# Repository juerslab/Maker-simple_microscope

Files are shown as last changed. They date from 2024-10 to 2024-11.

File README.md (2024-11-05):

# Name: simple_microscope
This microscope grew out of a need created by the pandemic, during Spring 2020. To implement a brownian motion lab for a biophysics lab course, I built microscopes similar to this, and the students carried out the experiment at their homes.

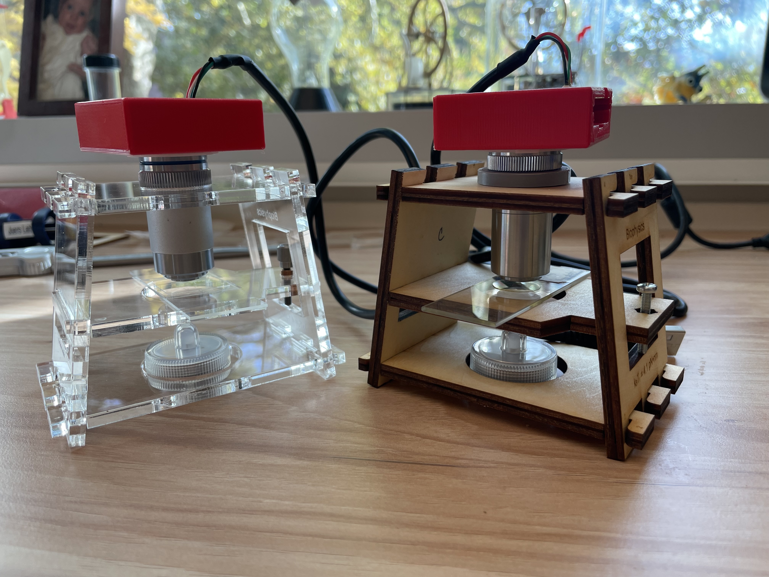
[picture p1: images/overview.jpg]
  

The microscope on the left uses acrylic and a fine adjuster. The microscope on the right uses plywood, a coarse adjuster, and the objective spacer (required for the second Amscope objective - see below)  

Microscope with image of 1 micron polystyrene beads imaged with the microscope:  

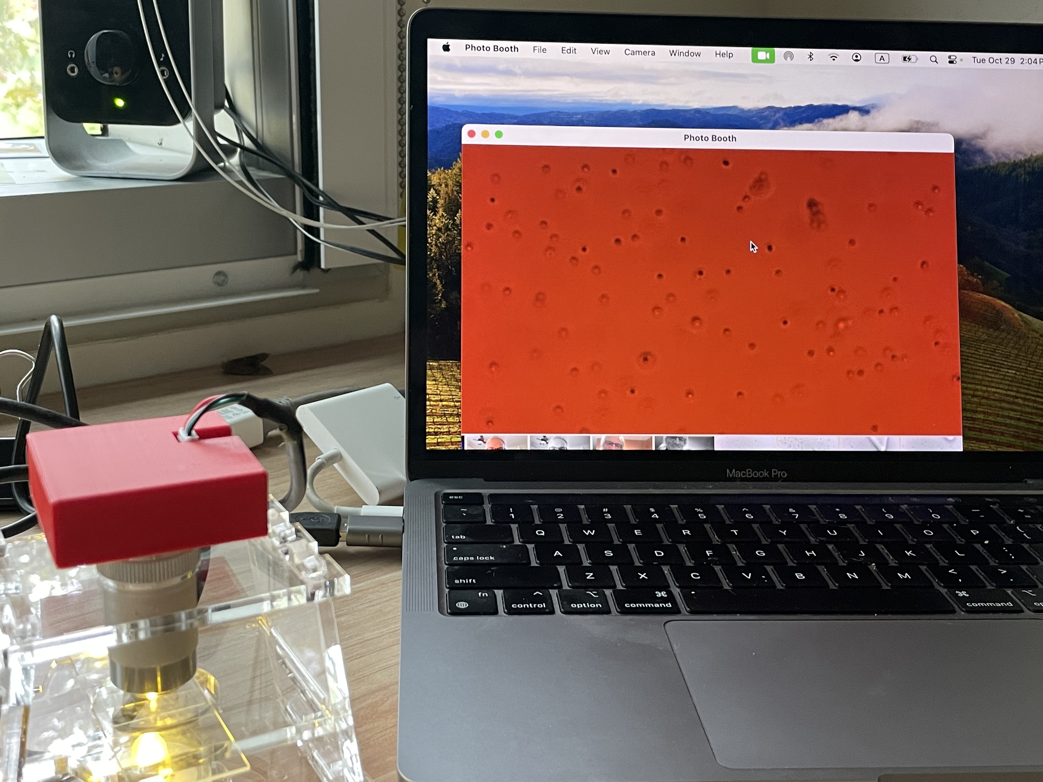
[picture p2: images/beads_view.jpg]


## Description & Parts
The microscope includes the following parts:

### Objective lens
The microscope is designed for an objective with RMS threading and a parfocal length of about 45 mm. We use these ~$25 objectives from Amscope:  
- https://amscope.com/products/a40x-v300?variant=40347660681391 
or:
- https://amscope.com/products/a40x-yx-v460 (This objective requires the use of a spacer; see below.)

### Camera

Arducam camera chip: (here ~$30)
https://www.amazon.com/dp/B07YHK63DS?ref=ppx_yo2ov_dt_b_fed_asin_title&th=1

### Light source

A small tea light works:
https://www.amazon.com/dp/B07654MKZH?ref=ppx_yo2ov_dt_b_fed_asin_title&th=1

### Camera housing

3D printed with an FDM printer. Also requires a 3D printed adapter for attaching the objective. 

### Framework

Laser cut from nominal 3/16" thick acrylic or plywood. 

### Vertical translation 

There are two options:
- Coarse:  Using a 20 mm M3x0.5 bolt with M3x0.5 mm nut
- Fine: Using a 25 mm M3x0.20 adjuster from Thorlabs
    - F3ES25
    - F3ESK1
    - F3ESN1P
    
### Misc parts (both 3D printed)

- Spacer ring if the second Amscope objective above is used
- Tool to help remove lens

## Creating the necessary parts. All parts were designed in OpenSCAD (see objects folder).
### 3D Printed parts
We print these with an FDM printer (Raise3D Pro 3 with hyperspeed option), using standard parameters. They are designed to be printed without supports, with the z-axis in OpenSCAD pointing up on the printer (this is the default orientation when the stl files are imported into IdeaMaker for the Raise3D printer.)
1. Camera housing
    - v3 is for the current model of the camera (11/24)
    - v1.1 is for an older model of the camera
2. Objective-camera housing adapter
3. Objective spacer (if using the second Amscope objective)
4. Camera lens remover (tool to help remove the lens from the camera)

### Laser cut parts - microscope framework
We cut these using an Epilog Zing laser cutter/engraver, using nominal 3/16" thick acrylic or plywood.The actual thickness of products we have used seems to vary enough that one needs to measure the thickness of each piece before cutting.  
1. Measure thickness of stock using caliper, in mm. 
2. Adjust parameters in OpenSCAD code.
3. Export to DXF
4. Import DXF file into CorelDraw or Inkscape. If using labels, there is a default coreldraw file called simple_microscope_labels_only.cdr which can be used as a template. The dxf file can be imported on top of the labels, and its position adjusted.
5. Cut/engrave.  For our 60W Epilog Zing, the following Speed/Power values were used for nominal 3/16" thick material:

Table to get main OpenSCAD parameters.

| Material | Design         | Main Slot Height | Sample Platform Slot Height |
|----------|----------------|------------------|-----------------------------|
| Acrylic  | Slot           | d + 0.36 mm      | d + 0.37 mm  (?)            |
| Acrylic  | Interlocking   | d + 0.42 mm      | d + 0.37 mm                 |
| Plywood  | Slot           | d + 0.27 mm      | d + 0.42 mm                 |
| Plywood  | Interlocking   | d + 0.47 mm      | d + 0.42 mm                 |

- The above parameters can be considered to be a starting point.
- Note that the above acrylic parameters assume a smooth edge. If the edge is somewhat rough, then add about 0.1 mm. In our experience cast acrylic tends to produce rougher edges, and needs to have a larger slot width.
- If the slots are too wide, the whole framework can be shimmed. (See below.)
- If the slots are too small, the framework will get "frozen" after locking and break when taking apart; plywood is more forgiving.
- Other parameters that may need adjusting include hex_nut_radius and fine_thread_cylinder_radius, depending on hex nut size and laser kerf
 
Table to get laser power (for Epilog Zing, 60 W)
| Material (3/16) | Raster  |  Vector  |
|-----------------|---------|----------|
| Acrylic         | S90/P25 | S35/P100 |
| Plywood         | S90/P30 | S70/P65  |

## Assembly

Two views of the microscope:  

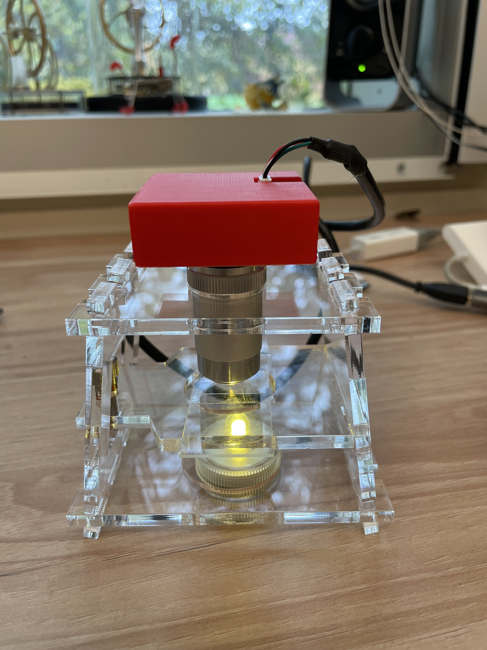
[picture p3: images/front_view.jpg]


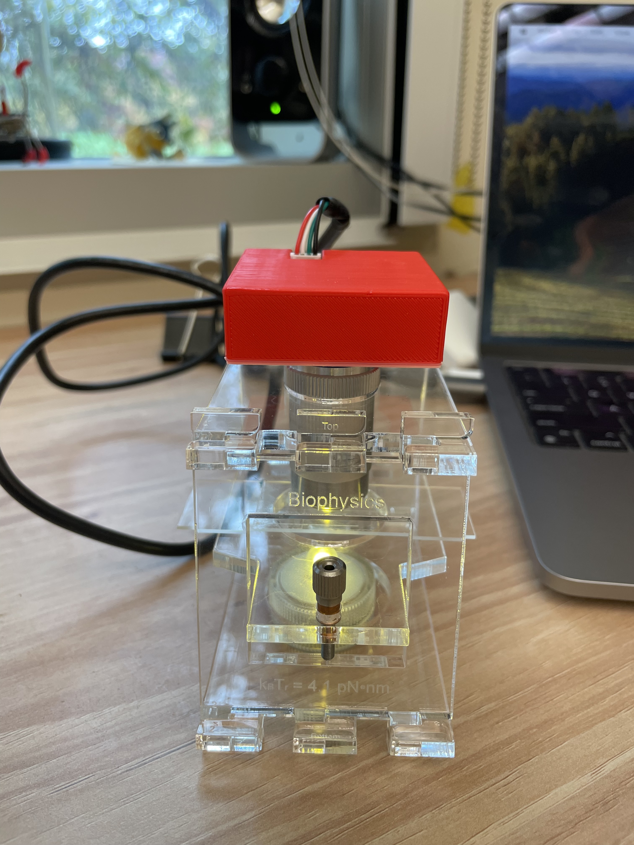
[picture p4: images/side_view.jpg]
  

### Step-by-step 
The parts of the microscope.  

  

1. The pieces interlock. Numbers indicate which pieces should be together. Attach the first side to the bottom and lock so that the 1s line up.   

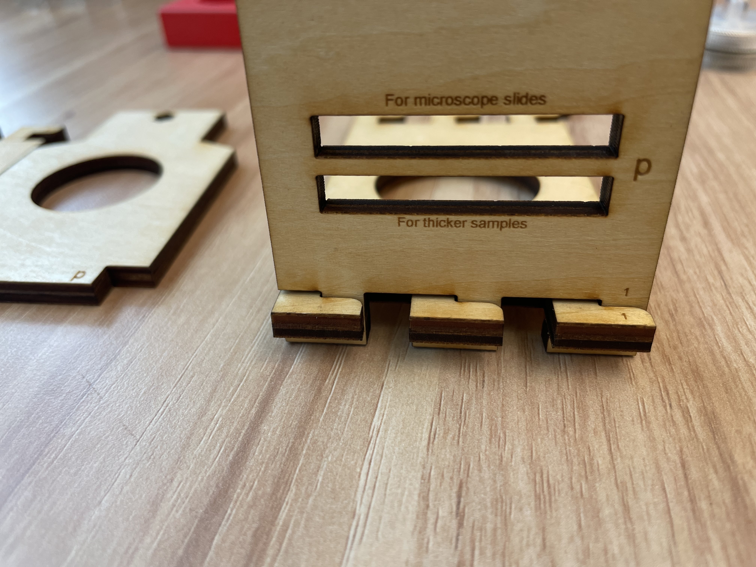
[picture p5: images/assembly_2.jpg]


2. Attach the other side.  
 
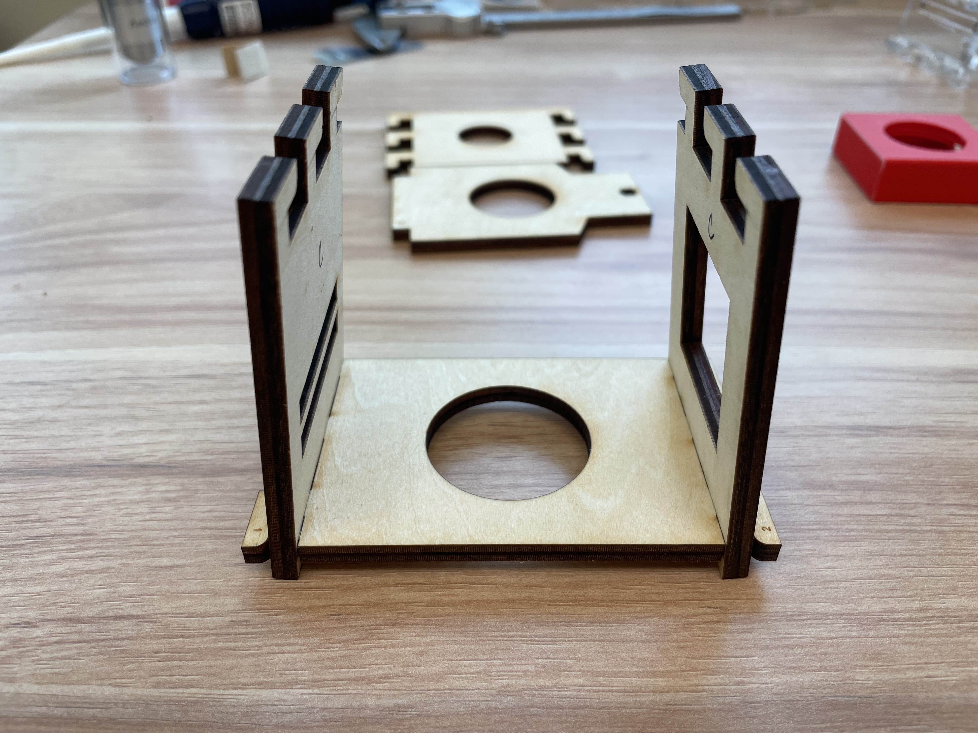
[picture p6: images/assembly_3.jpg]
  

3. Place the top onto both sides without locking.

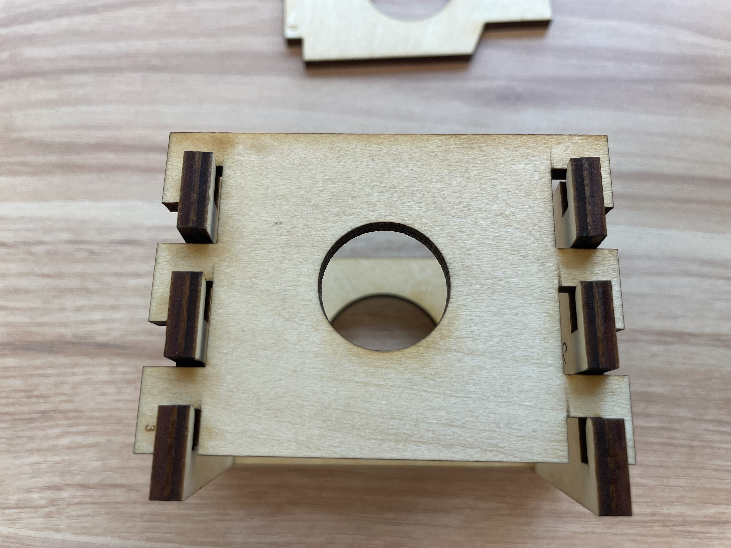
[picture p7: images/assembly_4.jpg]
  

4. Once the top is on both sides, then lock both sides simultaneously.

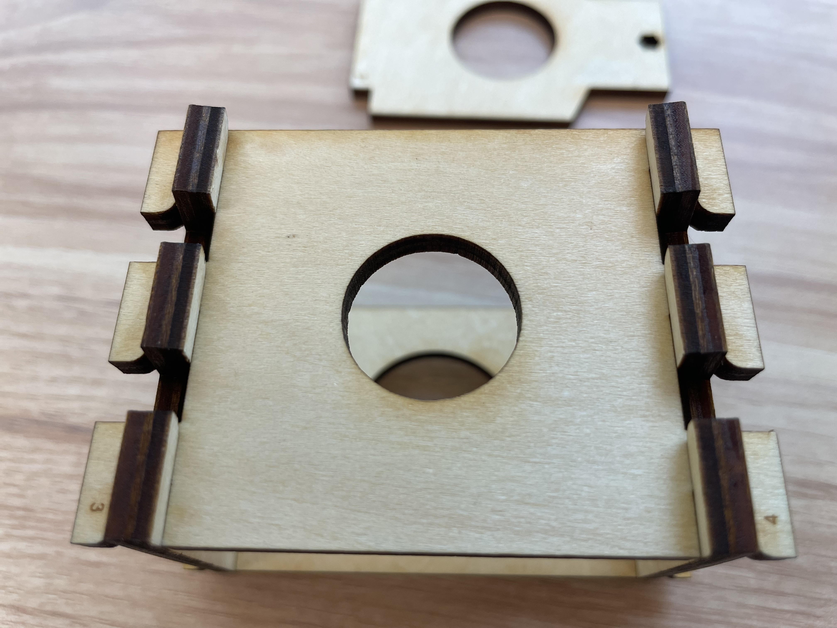
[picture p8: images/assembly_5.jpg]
 
   
5. The nut presses into a matching hold on the sample platform piece.

  

6. After pressing the nut in. If you use the fine adjustement, instead of a nut, you'll use a cylindrical sleeve.

  

7. Next slide the platform in so the tab with the nut enters the square hole on the side.

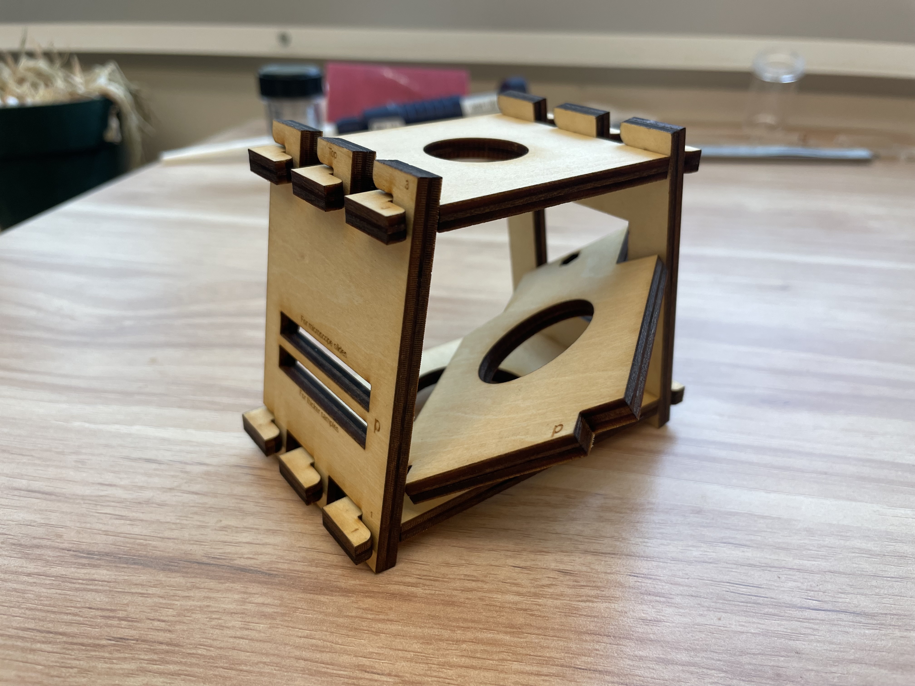
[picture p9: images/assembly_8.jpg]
  

8. Then place the other tab in the slot on the other side of the framework.

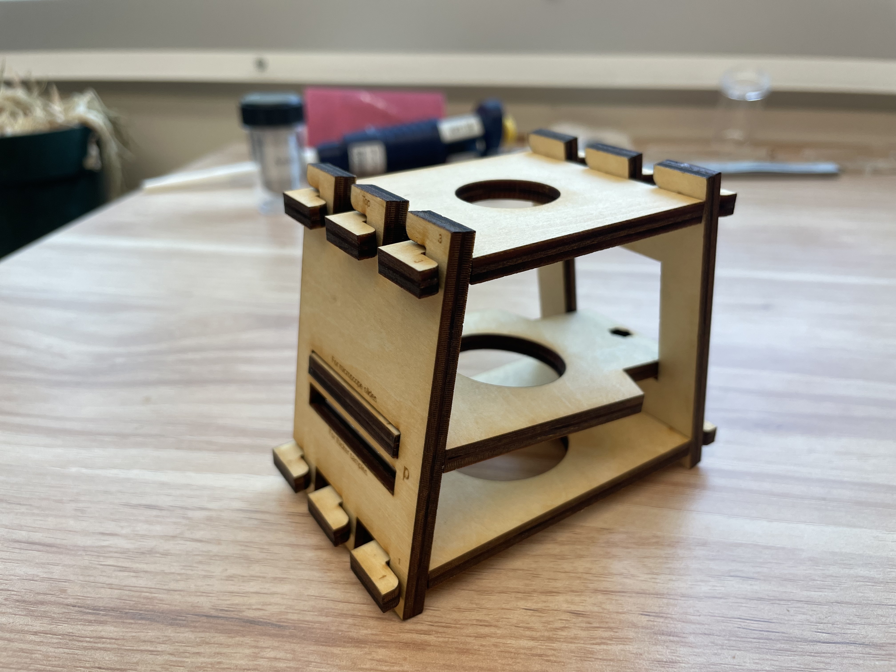
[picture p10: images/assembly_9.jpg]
  

9. Thread the bolt in the nut, and screw it in until the platform is level. The framework is finished. 

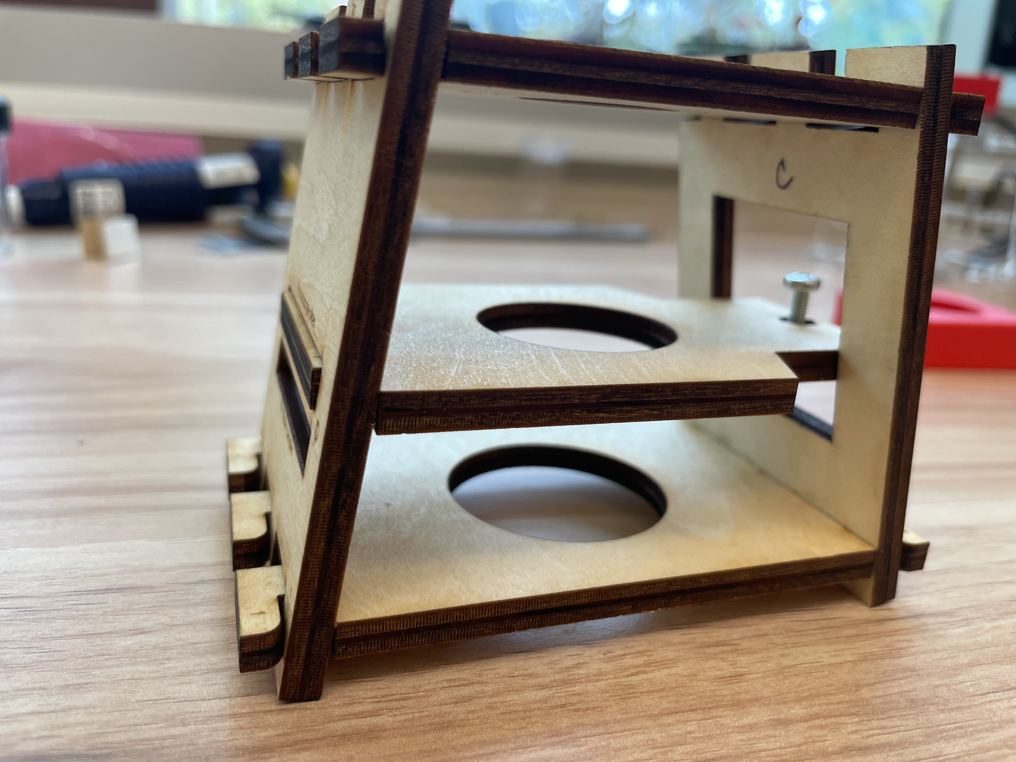
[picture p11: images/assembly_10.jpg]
  

10. The objective and objective_camera-housing adapter.

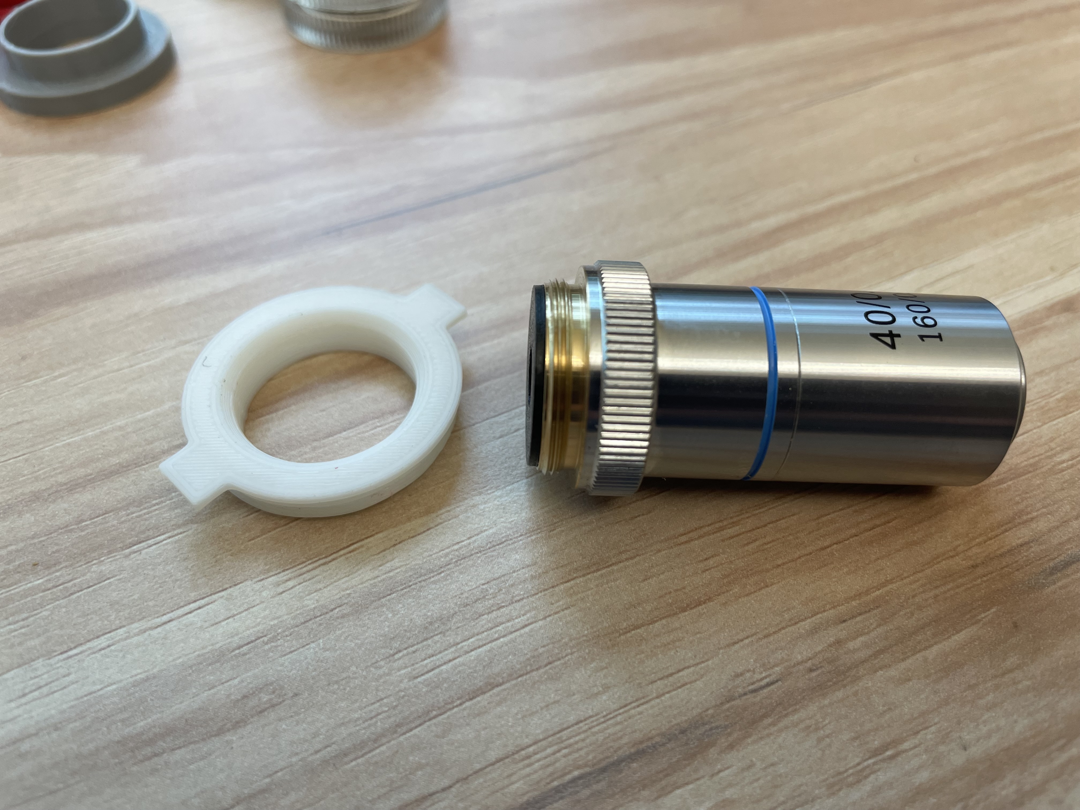
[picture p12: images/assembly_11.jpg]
  

11. Screw the adaptor onto the objective. Some fiddling may be required to get the threads correct. 
 
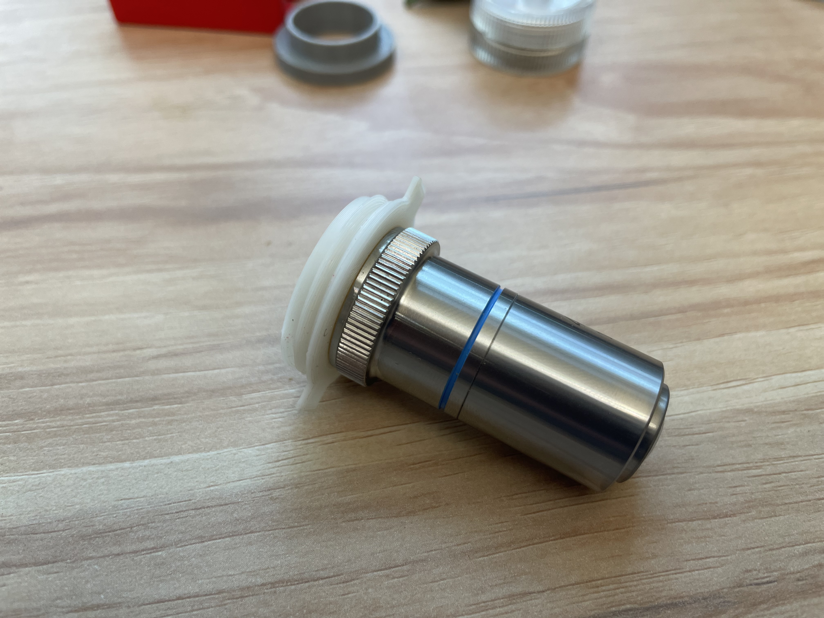
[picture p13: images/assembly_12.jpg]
  

12. Objective & adaptor with camera housing. Screw the adaptor into the camera housing.

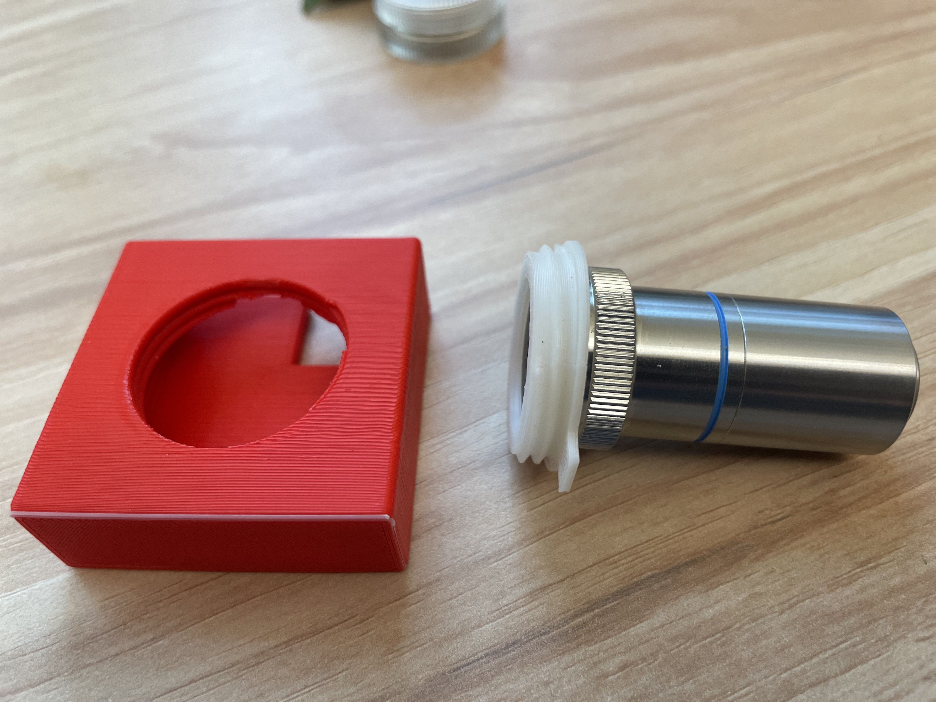
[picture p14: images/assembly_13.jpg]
  

13. Complete, waiting for the camera board.

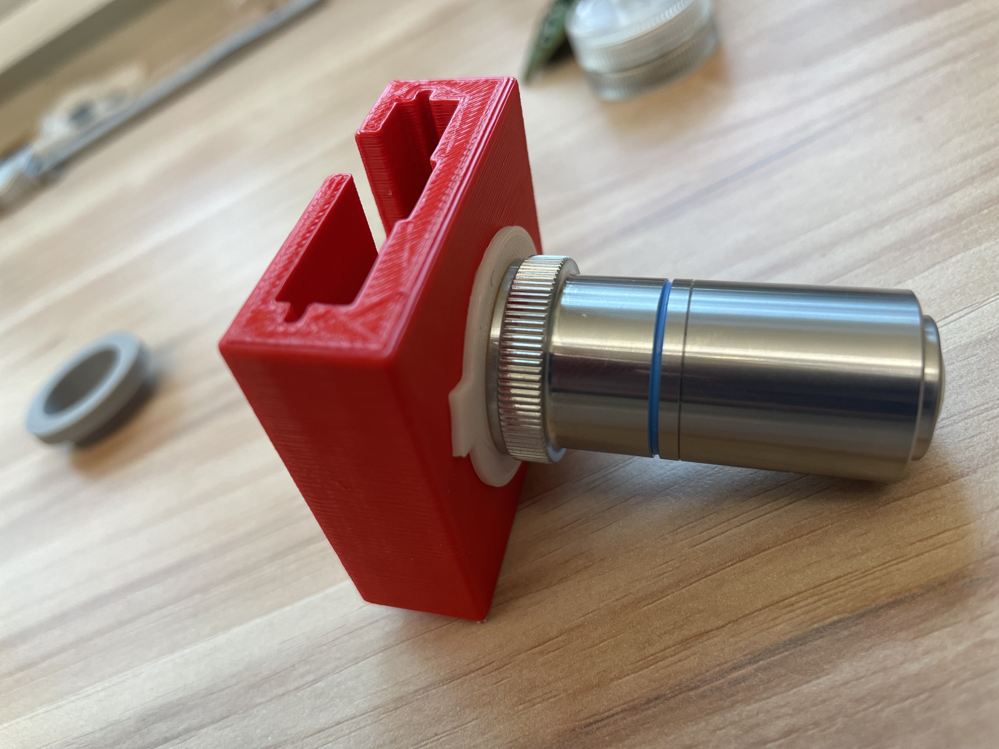
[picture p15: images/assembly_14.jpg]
  

14. Slot the camera board in. Be sure to remove the lens from the camera first. 

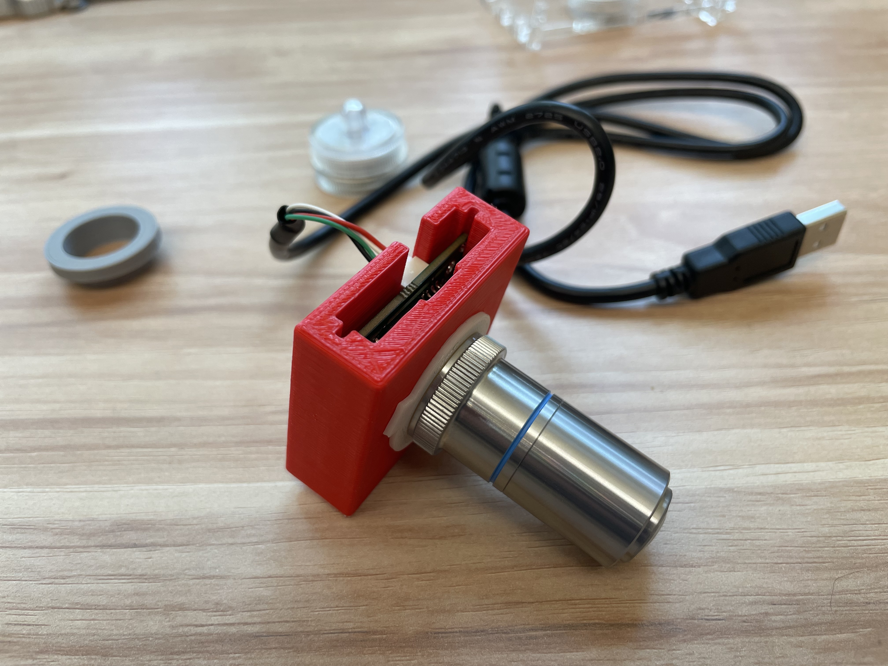
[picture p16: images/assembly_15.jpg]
  

15.With this objective, the objective spacer (grey) is needed. 
 
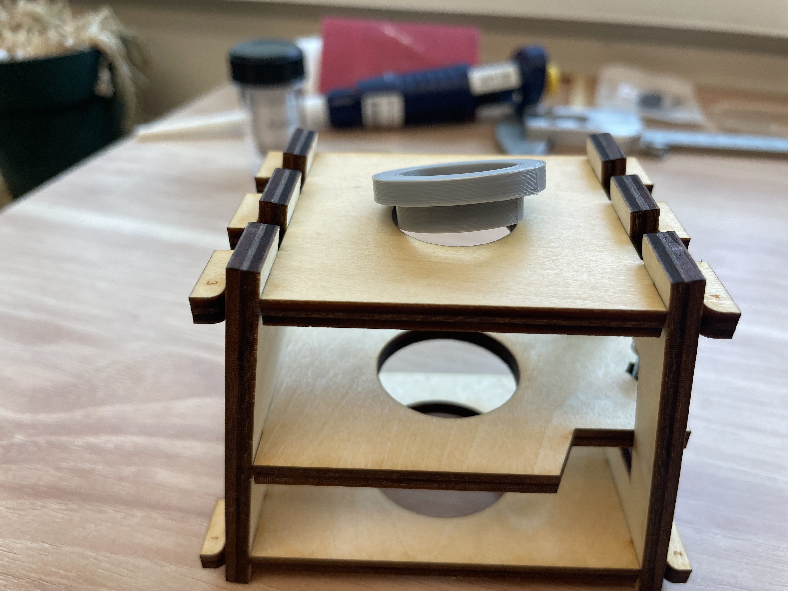
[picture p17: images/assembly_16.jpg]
  

16. Spacer inserted.

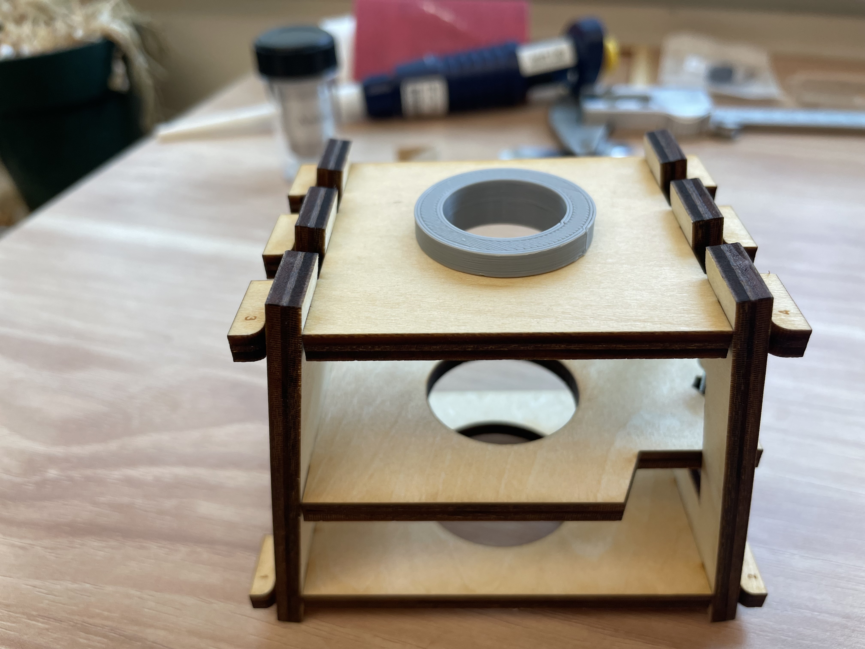
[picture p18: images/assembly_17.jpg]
  

17. Next insert the objective into the spacer (or hole in the top).

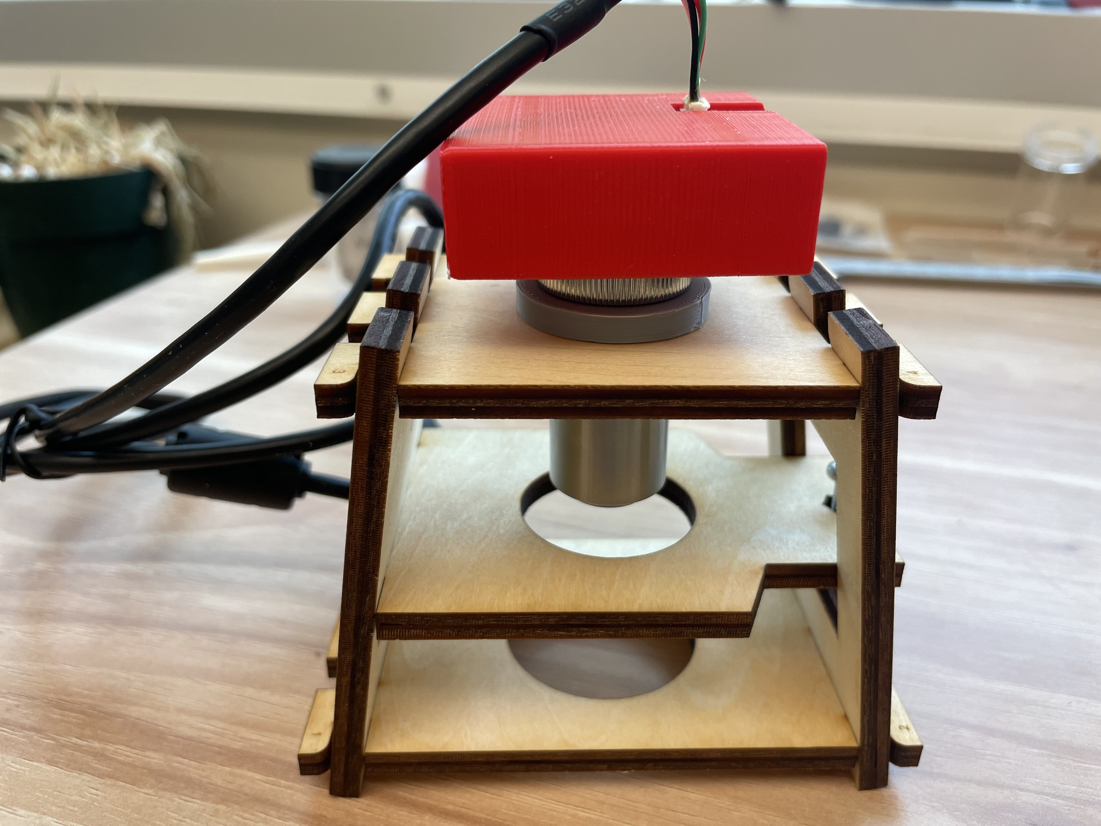
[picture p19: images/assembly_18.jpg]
  

Complete. 

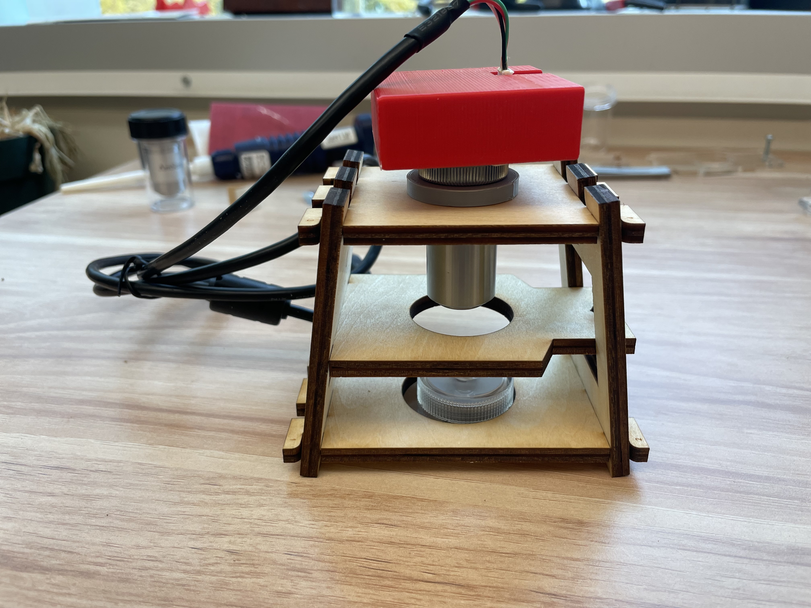
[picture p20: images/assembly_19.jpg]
  

With light source turned on.

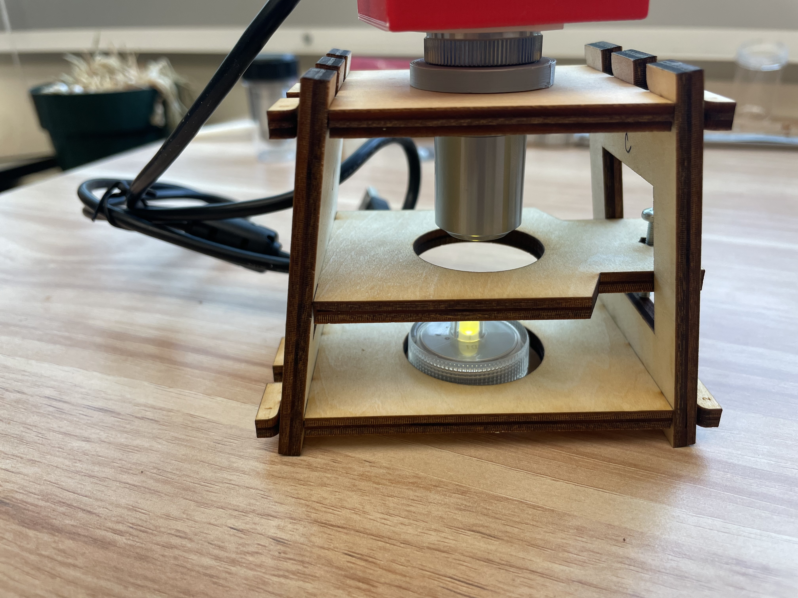
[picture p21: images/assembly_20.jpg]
  

Notes
- If the framework is loose, it can be shimmed by cutting and folding paper strips to get the right thickness, and inserting between bottom piece and sides in the middle interlocking piece. The platform can be shimmed with a piece of tape on the large tab.
- The light source is bright enough for good visualization of diffusing polystyrene spheres. Darker slides may require moving the light source closer to the sample, or a brighter light.

## Future work
- add a slide transport mechanism
- modify the framework design:
    - to be more robust to variations in stock thickness
    - prevent the objective from rotating in the top framework piece
- modify the camera housing design to have a latching mechanism to keep the camera chip fixed

## Authors and acknowledgment

## License

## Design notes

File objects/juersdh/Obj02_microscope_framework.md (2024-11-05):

# Notes for development of the microscope framework
9/24/2024
The framework is made of 4 pieces of laser cut 1/8" acrylic sheet, with a fifth piece used as a platform to hold the sample. The platform height can be adjusted finely on one side, and has two positions possible for the other side.   

Because the acrylic can be slippery, the rubber band used to hold the camera/objective adapter on the objective was also used to hold the framework together. Since I am obviating the need to hold the camera/objective adapter on the objective by threading the adapter, it would be nice if the framework held together in a different way.

If the framework is built out of plywood, it stays together pretty well without the rubber band. So I will be switching to plywood.

### Build aspects 
- plywood
- added numerical guides to aid in assembling framework
- added some other text on the framework
- increased height of window for adjusting hex bolt to make it easier for fingers to fit
- need to move out the hex nut hole just a bit 

9/25/2024

I did these things, and made a couple frameworks out of 1/8" plywood. However, a new(ish) problem appears, which is that the field of view oscillates. So I investigate these oscillations

### Oscillations

The amplitude appears to be perpendicular to the ~mirror plane of the framework. It's larger with the newer camera. When I tap the table, the oscillations are in this direction. The seemy to be worse with the wooden framework than the acrylic framework. If I add a rubber band around the framework they are a bit smaller. So it could be:
- the framework is less stiff in this direction
- the objective/camera combo swings in this direction

The wooden frame appears to be less stiff than the acrylic frame, when flexing in my hand.

#### Attempts to reduce the oscillations
- Putting the wooden frame on a piece of open cell foam improved things a lot.
- The amplitude also depends on the surface. On one table the oscillations are larger than on another table.

Tried using thicker stock - 3/16" acrylic. This worked quite well. So will switch to thicker. 
- Tried with 1/4" acrylic. But this seems less forgiving to bending, and will probably fracture after fewer cycles of assembly/disassembly.
- So 3/16" seems to be the way to go. The stuff I used was sourceone 0.18" thick by spec and 0.17" thick by caliper. I ordered more of this - will be here on monday. Will also try 3/16" plywood.

Would also be good to switch to fine thread bolts. For M3 coarse, the pitch is 0.5

#### Further work.
9/26/2024
Made adjustments to build the whole thing out of 3/16" acrylic. This seems to be ok. Possibly is more stable, but will need a bigger knob to turn than just the screw... (maybe a screwdriver, or one of these: https://www.thorlabs.com/thorproduct.cfm?partnumber=MAS20)
Probably should make the slot a little wider so there's less stress on the acrylic. 

9/29/2024
Working in 3/16" acrylic...
Increased the width of the slot to receive the 3/16" sample platform. 
- .45 cm was too small
- .5 was too large
- .46 seems ok - not much stress when in focus, but enough to keep things stable
** The problem could be that if the material is a different thickness it might not work very well.

Cutting some new frames.
for 3/16" acrylic:
-raster s90p25 is ok
-vector s40p100 leaves a ragged edge on a few
-vector s35p100 is better

for 3/16" plywood:
- raster s90p25 was a little dim
- raster s90p30 was a little better
- vector s70p50 didn't quite cut all the way through; maybe two passes?
- vector s70p60 did ok. Still need to punch things out, but not too much fire :)
- vector s80p60/raster s90p20 with two passes did ok for the engraving but too burnt for vector
- vector s90p40/raster s90p20 with two passes did ok for the engraving but too burnt for vector
- vector s70p65 seems good
- vector s70p70 seems too ragged on top surface

Note the new acrylic and plywood are a little thicker. So try wider slots.
for plywood:
- 5 mm wide slots were too narrow;
- 5.1 mm side slots were good

For the 0.187" acrylic
- 5.1 mm slots were a bit wide (ok, but not a tight fit)MiM
- 5.05 mm slots are good

There are thus several file sets, with varying slot heights

10/2/2024
Modified approach to use OpenSCAD, rather than manual building in QCAD. This will allow for simpler varying of the two key parameters. In Openscad, these parameters seem pretty good

10/3/2024
4.88 mm plywood
5.1/5.2 is a little tight
5.15/5.25 is a little better
platform:
main hole needs to move over
nut hole could be a little smaller

"Final" parameters

|Stock type	Thickness	Main Slot Height	Platform Slot Height		Nut radius	
Acrylic- 3/16" SourceOne.org X000CYOJ25 (newer)	4.69 mm/0.185"	5.05 mm		5.17 mm	3.00 mm
Acrylic- 3/16" SourceOne.org X000CYOJ25 (older)	4.25 mm/0.168"	
Plywood- 3/16" 									4.88 mm/		5.15 mm		5.30 mm	2.95 mm

10/7/2024
Trying a new design for the joinery - interlocking. This will hopefully fix the problem that the 
framework can just fall apart if it gets loose. This can be a problem especially with the 
acrylic framework. 
With plywood: 
Slot_height = 5.15. Too hard to assemble.
Slot height = 5.4. Too wobbly
Slot height = 5.25. Still very hard to assemble.
Slot height = 5.33. Still very snug (?)

10/8/2024
Getting the slots to initially slide is difficult. So I try to round the corners...
Slot height = 5.3 with rounded corners on tabs. Pretty hard to assemble...
Slot height = 5.35 with rounded corners on tabs. Still very hard to assemble?

Measuring slot heights with caliper.
Designed	Measured
5.15		5.15
5.25		5.25
5.3			5.26
5.33		5.4
5.35		5.41
5.4			5.44

Not sure if this design is good for plywood. Try with acrylic.

New sourceone 3/16. Thickness is 4.27 mm with caliper (not 4.69).

Try 5.3 - very wobbly
Try 4.9 - still wobbly
Try 4.5 - too tight! It broke when I disassembled it.

Not sure if this design is good for acrylic :)

Next sheet of sourceone 3/16" (4.33 mm with caliper)
Try 4.7 - this isn't terrible, but it actually not easy to get completely assembled. 

A couple possible solutions:
1. Use only two teeth for the top piece.
2. Make the teeth opening wider on the top piece, so only the teeth on the tops of the sides are engaging. 

Also need more reliable acrylic thicknesses. So I try a new source: 
https://www.canalplastic.com/
I ordered 3/16" cast acrylic. It's about $6/square foot + shipping (from NYC), which turns out to be cheaper than sourceone from Amazon.

10/10/2024
There are a couple problems here:
1. There appears to be about 10% variability in the thickness of the acrylic. For instance, from canalplastic: "Pre-cut sizes are nominal and subject to a +/- 1/8" cutting tolerance." I'm guessing that the thickness variation for 3/16" plywood is less.
2. The acrylic has pretty high friction with itself.

Current parameters/procedure for nominal thickness of 3/16. Measure the thickness of the stock (d in mm). Then create files according to the following:
| Material | Design         | Main Slot Height | Sample Platform Slot Height |
|----------|----------------|------------------|-----------------------------|
| Acrylic  | Slot           | d + 0.36 mm      | d + 0.37 mm  (?)            |
| Acrylic  | Interlocking   | d + 0.42 mm      | d + 0.37 mm                 |
| Plywood  | Slot           | d + 0.27 mm      | d + 0.42 mm                 |
| Plywood  | Interlocking   | d + 0.47 mm      | d + 0.42 mm                 |

- Redo code to output all 5 pieces at once. I had to reduce the overall width to 57 mm from 60 mm to get the whole shebang to 
be less than 12" wide.
- Try interlocking with d=4.32 mm; main slot height = platform slot height = 4.80 mm; this was pretty good for assembly, but the platform slot height was a little too big.
- Try again with 4.8, 4.75. This is pretty good. But the lower platform slot is tight. Need to drop down the lower limit of the right side about 1-2 mm. 

10/11/2024
- Increased the window height on the right side.
- Added the option to print text within openscad. I'm not sure the most efficient approach. Printing the text in openscad requires selecting and editing the linewidth of all the text in coreldraw once imported. It might be easier just to type the text in coreldraw. Two workflows:
1.
    - Export pieces from openscad as dxf without labels
    - Import into coreldraw. Add labels in coreldraw.
2.
    - Export pieces from openscad as dxf with labels.
    - Import into coreldraw. Select labels and increase linewidth so the labels are engraved.

I think workflow 1 is the way to go. It's a lot of work to select the labels each time when tweaking things. I have a labels template in coreldraw that can be used to import labeless pieces into, and then position in place by hand. 
It would be interesting to see if one can specify the linethickness in the dxf file. 
Now producing a few in acrylic that's 4.32 mm thick.
4.8 for main slot height is a bit too large - the framework is a bit wobbly
4.75 is also a bit too large for the platform slot height - the sample platform barely flexes at parallel to the top plate
But 4.7 is to small - it broke when I was disassembling it. 

In the end, I went with main height = 4.75, platform height = 4.70 (for d=4.33 mm). So we have constants of 0.42 mm and 0.37 mm.

10/15/2024
Producing a few in plywood (assume 4.55 mm thick.)
I will first try as above:
4.55 + 0.47 = 5.02 for main slot height
4.55 + 0.42 = 4.97 for platform slot height

The parameters above for speed & power didn't really work for this one. So I do two passes.
This was too much - ended up too burnt.
Also too narrow. So try: 5.12/5.07 and 90/35 70/70 for speed/power for raster & vector.
This seems pretty good. But still doesn't cut all the way through. So I try moving focus further down.

The next two pieces of plywood were 5.00 mm. So I use 5.47/5.42 mm, and this is pretty good. So the constants above seem ok.

One problem, though, is that the plywood thickness appears to vary even up to 0.2 mm within a single board. 

11/4/24
Some new acrylic came in (from Canal Plastics, cast acrylic). Measured to be 4.39 mm thick. Tried to cut a framework using the above parameters (4.81 mm & 4.76). The fit was too tight. Even with 4.86 & 4.76 it was too tight. One possible reason is that the surface was rather rough, even at 5000 Hz. I'm wondering if this could be a cast vs extruded. Some websites suggest that extruded acrylic cuts with a smoother edge. According to a comment in Amazon, the acrylic I was using previously (from sourceone.org) is extruded acrylic. So this appears to mean that there is an additional offset if the acrylic is cast...
11/5/24
Trying again with the new acrylic. This sheet measures 4.50 mm. Using the above, I would get 4.92 & 4.87. But I will try 5.12 & 4.92 instead. 
- 4.92 seems ok, but 5.12 is a little big. 
Try 5.07 & 4.92
- The weird thing here is that 5.07 makes it seem looser...

So I think the take-home messages are:
- that the above parameters are likely a good starting place 
- if the acrylic is case, possibly increase by 0.1 mm. 
- plywood will probably be more forgiving

Next I see if there's a way to make the wobbly frameworks more solid.
- Shimming works, although not super pretty. Folding paper strips and inserting between bottom piece and sides in the middle interlocking piece. This is enough. Need to play around with the appropriate thickness.

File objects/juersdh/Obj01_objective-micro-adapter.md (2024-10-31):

# Parts for simple_microscope (3D printed)
## Objective - camera housing
### Version 1
For the initial camera board.
9/25/2024
Am updating this to include threads (see below in Version 3)

### Version 2
For the next generation camera board, which has a somewhat different formfactor.

### Version 3. (Sept 2024). 
Wanting to update the design to include threads for the objective. In V1 & V2, the objective is held onto the adapter with a rubber band. Using threads may make this more stable.

For the threads, I'm using the BOSL2 library. The RMS threads on the objective are pretty fine, and it seems that using the Raise3D printer yields decent RMS threads only when the thread axis is perpendicular to the build plate. This in turn then requires supports. So I will be trying two different variants of Version 3.

#### Version 3a
The adapter will include rather than a cylindrical hole for the object, a threaded cylindrical hole to receive a threaded ring that the objective will be attached to. The code is something like this:

##### Main body
For the main body:
difference(){
    cube([length,width,depth+2]);
    translate([(width-cwidth)/2-0.5,(width-cwidth)/2-2.0,depth-5])cube([cwidth+1,cwidth+1+10,2]);//board slot - new
//    translate([(width-cwidth)/2-0.5,(width-cwidth)/2-0.5,depth-5])cube([cwidth+1,cwidth+1+10,2]);//board slot - old
    translate([(width-cwidth)/2+2.0,(width-cwidth)/2,depth-9])cube([cwidth-4,cwidth+10,4]);//opening below
    translate([(width-cwidth)/2+2.0,(width-cwidth)/2,depth-3])cube([cwidth-4,cwidth+10,2]);//opening for electronics on top of board
    translate([width/2-5,width/2,depth-10])cube([10,width/2,2]);//opening for camera   
    **translate([width/2,width/2,(depth-7)/2]) threaded_rod(d=1.2*25.4,l=depth-7,pitch=2); // threaded opening to receive objective ring**
    translate([width/2-10.65,30.5+1.0,8])cube([8.0,20,100],center=false);//opening for usb cable connector - new only}

Next, camera board slides in easily, but also slides out easily. Need either a tighter fit or some kind of latching mechanism. First try tighter fit by reducing slot size.
- 2.0 mm - too large (in & out easily)
- 1.6 mm - too thin (can't get in)
- 1.8 mm - too large by a smidge
- 1.7 mm - this is pretty good. It goes in relatively smoothly and then stays put. (Sometimes - other times too tight.)
- 1.75 mm - seems better(?) 

9/23/2024
Next, it would be nice to have rounded corners. This can be done with the BOSL2 library.
Also move the opening for the USB connector over to try to center camera better:
- 0.2 mm - this actually looks off center; so I go back to zero.

Rounded corners with radius 1 are ok. radius 2 looks better, except on the surface contacting the build plate. The brim seems stuck. So I go back to 1.

## Objective - camera housing adapter
And the objective ring:
difference(){
    translate([0, 0, 0]) threaded_rod(d=1.2\*25.4-0.5,l=hole_depth,pitch=2);
    translate([0,0,0]) threaded_rod(d=0.8*25.4+0.5,l=hole_depth,pitch=0.7055,
        ibevel=false,bevel=false,$slop=0.05,$fa=1,$fs=1);}

Note: RMS threads are 36 threads per inch, which translates to a pitch of 0.7055 (25.4 mm/36). For the other side I picked a pitch of 2 randomly - just something larger than 0.7. 
One tricky part is getting the diameters correct. The female and male parts can't have the same diameter or the male part gets stuck. I try a few fudge factors. 

For the RMS threads:
- 0.7 mm is too large. The objective slides off and on easily.
- 0.6 mm is pretty good. The objective slide on a ways, and then screws on completely.
- 0.5 mm is too small. The threads engage immediately but the objective doesn't screw on completely.

Possibly I need to go to the next decimal place to optimize the fit. I also wonder if beveling would help limit the cross threading which seems to be hard to avoid.

For the outside threads:
- 1.0 mm is too small. The threads engage immediately, but the ring doesn't screw on completely.
- 1.5 mm is pretty good. The threads engage immediately and the ring can be screwed completely through the hole.

Added a stop to prevent the ring from going to far into the main body.

Settled on 1.5 mm and 0.6 mm.

Now trying intermediate values.
- 0.58 - 0.50. Actually 0.50 appears to work, except theres a hard spot to screw past. Once past that, though, the threads are then loose. I try to eliminate this hard spot by adding a bevel. This worked. So now try smaller values:
- 0.48 - pretty good. Goes on smoothly, but a little lose 
- 0.45 - Goes on a little hard.
- 0.46 - This is good. Goes on smoothly without much play.

9/24/2024
Add tabs to make it easier to remove.

## Objective vertical spacer
There are two (at least) different objectives from Amscope, with slightly different shapes. The skeleton is made for one of the
shapes, and this adapter is needed for the other shape.
- Looks like it's raising the objective too high. Reduce height by a couple mm?
    - Current spacer is 5 mm. Try 4 mm & 3 mm.
    - 4 mm is pretty good, for 1.54 mm slide (1.73 mm w/ coverslip) and 1.17 mm slide (1.27 w/ coverslip); works also for a bead slide (1.18 slide, 1.34 mm with coverslip)

## Camera lens remover
No changes were made to this file.

10/17/2024
Checking that slides with beads work.
- Mounted a VWR "1 mm" slide (1.18 mm with caliper) with doublesided tape & coverslip (1.34 mm with coverslip). This visualized just fine.

Other troubleshooting
On some cameras there are specks, which appear to be dust or defects in the camera...
- Hitting these with compressed air reduced the number of specs, but not compeltely. This will be a problem for a brownian motion
lab, since the specs look like fixed polystyrene beads...
- Three were bad. One was recoverable. It would be best to keep the cameras in the antistatic back they come in...

Nearly finished. Things to check/keep in mind/do:
1. Check all boxes for parts.
2. Create parts list and directions to go in boxes (maybe this can be Bassant)
3. Note that the platform nut hole could shift a bit in.
4. Create slide transport thing that can clamp to the slide platform.
5. Find M3-fine threaded nuts & 20 mm bolts.
6. Print more objective rings when white filament comes in.
7. Get more 20 mm coarse threaded bolts.

10/23/2024
Parts from Thorlabs cam in for M3x0.2 bolts. Try them out.
These seem to work ok. I am using:
F3ESN1P threaded bushing pressed into the platform
F3ES20 threaded rod; but this is too short to use with F3ESN1P, so switch to F3ES25
F3ESK1 knob, which when friction fit tightly seems to not come loose.

So I order more of these parts for the rest of the microscopes (for 8 setups in all).

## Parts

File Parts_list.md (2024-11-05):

Parts list for simple_microscope
1. Framework (5 or 6 pieces)
2. Nut and/or copper sleeve
3. Bolt and/or microadjuster
4. Objective lens
5. Camera
6. Camera housing
7. Objective-camera housing adapter
8. Light source
9. Lens removal tool
(10. Objective spacer - for one objective type)

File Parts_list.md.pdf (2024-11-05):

/Users/juersdh/Docs/GitHub/repos/maker-simple_microscope/Parts_list.md | Page 1/1
Saved: 11/5/24, 11:13:28 AM | Printed for: Doug Juers
Parts list for simple_microscope
1. Framework (5 or 6 pieces)
2. Nut and/or copper sleeve
3. Bolt and/or microadjuster
4. Objective lens
5. Camera
6. Camera housing
7. Objective-camera housing adapter
8. Light source
9. Lens removal tool
(10. Objective spacer - for one objective type)

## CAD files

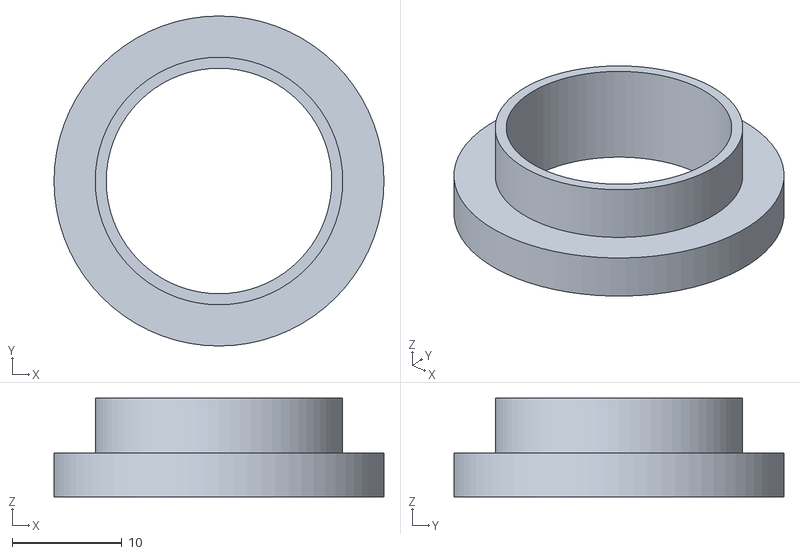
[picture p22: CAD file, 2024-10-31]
3D_Printed_Parts/stl/Objective_spacer.stl
30.0 x 30.0 x 9.00

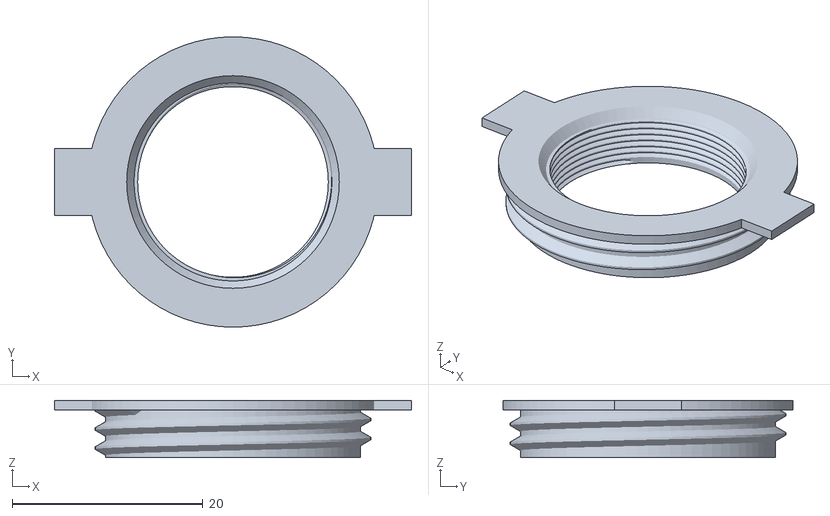
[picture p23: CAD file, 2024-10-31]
3D_Printed_Parts/stl/Objective_camera-housing_adapter.stl
37.5 x 30.5 x 6.00

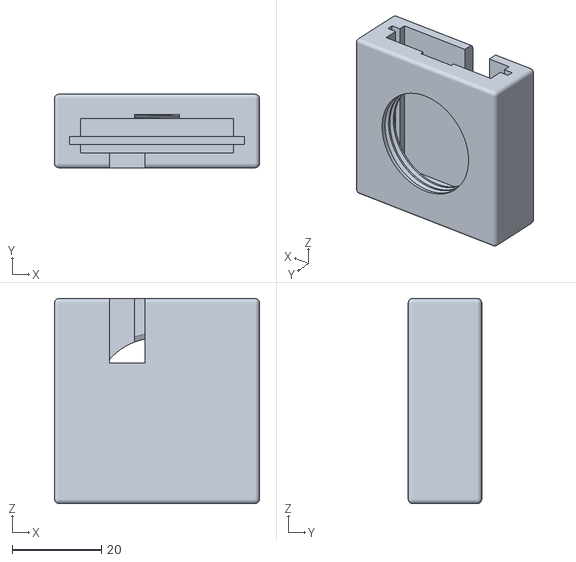
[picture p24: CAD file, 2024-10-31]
3D_Printed_Parts/stl/Camera_housing_v3.stl
46.0 x 16.5 x 46.0

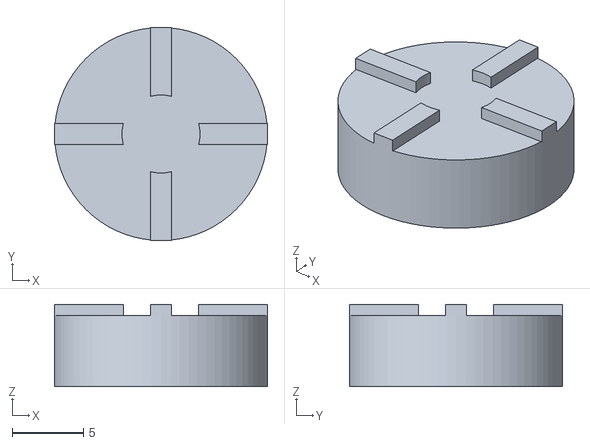
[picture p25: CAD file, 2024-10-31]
3D_Printed_Parts/stl/Camera_lens_remover.stl
15.0 x 15.0 x 5.80

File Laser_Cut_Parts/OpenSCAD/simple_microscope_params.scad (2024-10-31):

// Variables that determine the geometry of the microscope;
// 
$fn=36;
overall_width = 57;
side_height = 80;
top_length = 80;
bottom_length = 100;
obj_circle_d = 22.4;//Nominal diameter of objective
light_circle_d = 35.0;//Just needs to be wide enough for the light source
sample_circle_d = 30.0;
hex_nut_radius=3.0;//For hex nut
fine_thread_cylinder_radius=2.425;//For thorlabs fine thread cylinder (F3ESK1)
num_sides = 60;//6 for hex nut; 60 for thorlabs fine thread cylinder
nut_center_distance = 75.8;
stress_relief_r = 0.2;
main_slot_width=40;
main_slot_height=4.8;//Needs to be slightly larger than the thickness of the material (accounding for the kerf on the laser cutter)
// Rough values are 5.05 
sample_platform_slot_width=40;
sample_platform_slot_height=4.75;//Needs to be slightly larger than the main_slot_height
center_slot_width=34;//For "right" side, and for tab on sample platform
center_slot_height=34;// For "right" side
// Parameters for interlocking joinery
interlocking_joinery=true;
outer_height=5;
num_slots=3;
w=overall_width/(2+(num_slots-1)*3);


 

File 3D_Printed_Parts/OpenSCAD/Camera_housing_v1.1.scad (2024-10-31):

// Adaptor to hold camera over objective lens
$fa=5;
$fs=0.1;
width=40;// 
length=40;// 
depth=14.5;//
cwidth=33;//camera board width
objdia=20.25;//nominal diameter of objective threads
include <BOSL2-master/std.scad>
include <BOSL2-master/threading.scad>
//for makerbot this is too small
difference(){
    translate([length/2,width/2,(depth+2)/2]) cuboid([length,width,depth+2],rounding=1);
    translate([(width-cwidth)/2,(width-cwidth)/2,depth-5])cube([cwidth,cwidth+10,1.78]);//board slot
    translate([(width-cwidth)/2+1.5,(width-cwidth)/2+1,depth-9])cube([cwidth-3,cwidth-2+10,4]);//opening below
    translate([(width-cwidth)/2+1.5,(width-cwidth)/2+1,depth-3.22])cube([cwidth-3,cwidth-2+10,2.25]);//opening for electronics on top of board 
    translate([width/2-5,width/2,depth-10])cube([10,width/2,2]);//opening for camera   
    translate([width/2,width/2,7/2]) threaded_rod(d=1.2*25.4,l=7,pitch=2);//Threaded opening to receive objective ring
//    translate([width/2,width/2,0])cylinder(depth-7,d=objdia+1);//Original unthreaded opening

 
    translate([width/2,width/2,0])cylinder(5+2,d=20.25+1);

}

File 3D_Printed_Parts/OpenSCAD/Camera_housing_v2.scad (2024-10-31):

// Adaptor to hold camera over objective lens
// Camera is the Arducam X002BU078X
// There is an old version and new version.
$fa=5;
$fs=0.1;
width=46;// Old:40/ New: 40
length=46;// 
depth=14.5;//13.5 was the original.14.5 is the default...
cwidth=38.3;//camera board width: Old: 32.2 / New: 38.5
objdia=19.75;//nominal diameter of objective threads (20.25 first; then decrease...)
//for makerbot this is too small
difference(){
    cube([length,width,depth+2]);
    translate([(width-cwidth)/2-0.5,(width-cwidth)/2-2.0,depth-5])cube([cwidth+1,cwidth+1+10,2]);//board slot - new
//    translate([(width-cwidth)/2-0.5,(width-cwidth)/2-0.5,depth-5])cube([cwidth+1,cwidth+1+10,2]);//board slot - old
    translate([(width-cwidth)/2+0.5,(width-cwidth)/2,depth-9])cube([cwidth-1,cwidth+10,4]);//opening below
    translate([(width-cwidth)/2+0.5,(width-cwidth)/2,depth-3])cube([cwidth-1,cwidth+10,2]);//opening for electronics on top of board
    translate([width/2-5,width/2,depth-10])cube([10,width/2,2]);//opening for camera   
    translate([width/2,width/2,0])cylinder(depth-7,d=objdia+1);
    translate([width/2-10.65,30.5+1.0,8])cube([8.0,20,100],center=false);//opening for usb cable connector - new only
    

}

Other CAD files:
3D_Printed_Parts/OpenSCAD/Camera_housing_v3.scad
3D_Printed_Parts/OpenSCAD/Camera_lens_remover.scad
3D_Printed_Parts/OpenSCAD/Objective_camera-housing_adapter.scad
3D_Printed_Parts/OpenSCAD/Objective_spacer.scad
Laser_Cut_Parts/OpenSCAD/simple_microscope.scad
